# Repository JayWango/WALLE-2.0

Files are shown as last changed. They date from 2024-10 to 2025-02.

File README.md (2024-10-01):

<p float="left">
  
   
</p>

### Stereovideographic & Macromolecular Acquisition of Low-Light Emitters

The UCSB Oakley Evolution Lab seeks to investigate the evolutionary history of bioluminescence courtship signaling of small crustaceans called ostracods. Such emissions occur after nightfall when there is no moonlight and are characterized as pulses that vary in temporal and spatial patterns between species. We are creating a camera and DNA collection system named Stereovideographic & Macromolecular Acquisition of Low-Light Emitters (small-e), for deployment at the bottom of the Caribbean Sea. Small-e will capture stereo-vision video that will be stereo-rectified to create 4D models of the courtship patterns. We are aiming to have small-e be compact and to support new features compared to previous camera systems, such as time-precise light intensity measurements, time correspondent eDNA collection, and a 12-hour runtime. 

# External Behavioral Specification
The videography system will record stereo video footage of the ostracod courtship signaling. This data will be reconstructed into 3D models of the signals. Light intensity measurements of the signals will be made with a SiPM. This data will be output into a processable text file. The footage and light intensity measurements cause the DNA collector system to pump water through DNA collecting filters. The pump system will measure the amount of water processed to ensure proper collection.

## Low-Light Electrostereo Videography System
Stereo synchronized cameras will provide stereo vision video for reconstructing 3D bioluminescence courtship signaling of ostracods over time. This footage will be used to recognize patterns from courtship.

## DNA Collector System
At set timer intervals, a pump will push water through a filter to collect the DNA present in the water. 3 filters will be used to sample a total of 6L over the course of 12 hourss. The lab will be able to extract the ostracod DNA from the various species present in the water at different times corresponding to the video footage.

## Light Intensity Measurement
Detects the blue light intensity from the ostracod courtship signaling and outputs it into a file. Will help characterize the temporal patterns of the pulses among ostracod species. 

# Block Diagram 

small-e Block Diagram

# Team Member Responsibility 
- Ebony (Leader) - Programming the SiPM sensor to detect BioLuminescent light under water. Designing waterproof case suitable for SiPM Sensor.
- Reiley - Implementation of low-light, stereo camera system and synchronization.
- Roberto -  Designing DNA collector. Configuring the software interface of the pump system. Designing modular waterproof case for this system. 
- Ryan - Implementing user interface for utilizing the entire system as well as other general responsibilities, including the data storage system.
- Sammy - Implementation of low-light, stereo camera system and synchronization and SiPM.

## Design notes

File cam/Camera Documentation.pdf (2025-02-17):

## Watec 933 Camera Documentation

Curated by Dakota Barnes, 5/31/2024, dakota@casabarnes.com

1) New Camera Spreadsheet
https://docs.google.com/spreadsheets/d/1HkeTYAVQ3RaVRUFHyAiKlf5FlizRkfooBxWkuCNOLkc/edit#gid=0 (https://docs.google.com/spreadsheets/d/1HkeTYAVQ3RaVRUFHyAiKlf5FlizRkfooBxWkuCNOLkc/edit#gid=0)
2) Watec User Manual
https://drive.google.com/file/d/1hmxL5e7SJMkztWb8NpXOMxQa4R7WxiXF/view?usp=sharing (https://drive.google.com/file/d/1hmxL5e7SJMkztWb8NpXOMxQa4R7WxiXF/view?usp=sharing)
3) All_reset.bin
https://drive.google.com/file/d/1d34jDYIjwuBzf9ph53bu5fn5DB1mxrl5/view?usp=drive_link (https://drive.google.com/file/d/1d34jDYIjwuBzf9ph53bu5fn5DB1mxrl5/view?usp=drive_link)
4) Camera settings
https://drive.google.com/drive/folders/1ein_ycJGoXDxwvxqVLbZZHRgHMuEGonK?usp=drive_link (https://drive.google.com/drive/folders/1ein_ycJGoXDxwvxqVLbZZHRgHMuEGonK?usp=drive_link)

Quick Note

These settings were created in 2024 to get the SMALLE devices up and running. We spent a few weeks troubleshooting the cameras, as they were not able to connect. We got smalle 1.1 to work by just switching the left and right cameras, but we were not as lucky with Smalle 2 and 4. I believe the cause of the problems was that the cameras reset to default/previous IP addresses, which caused some conflicts when trying to connect them to the Jetson Nano. My advice for future engineers; just do the hard reset if you are spending too much time debugging. I was initially scared to do it but it is not as bad as it seems.

All Cameras Login for Accessing Settings (Typing IP address into connected browser)

Username = smalle

Password = smalle

Also current settings are just default, with brightness set to 15/20.

### A. Jetson/Camera Configurations

One of the changes that I made was to standardize the IP addresses across all left cameras, right cameras, and the Jetson IPv4 settings. Here is the table with the current camera information, and what their corresponding IP addresses should be.

Camera Physical Label | Side | Old Camera Label | SMALLE | Mac Address | Serial Number | Camera IP | Working
SMALLE 1 | LEFT | DNE | 1 | c4:7c:8d:30:62:70 | W51400625 | 192.168.0.250 | Yes
SMALLE 1 | RIGHT | DNE | 1 | c4:7c:8d:30:62:58 | W51400601 | 192.168.0.251 | Yes
SMALLE 4 Watec 8 | LEFT | oakley-watec5 | 4 | c4:7c:8d:30:63:38 | W51400825 | 192.168.0.250 | Yes
SMALLE 4 Watec 9 | RIGHT | oakley-watec4 | 4 | c4:7c:8d:30:63:37 | W51400824 | 192.168.0.251 | Yes
SMALLE 2 Watec 4 | LEFT | oakley-watec6 | 2 | c4:7c:8d:30:63:20 | W51400801 | 192.168.0.250 | Yes
SMALLE 2 Watec 5 | RIGHT | oakley-watec9 | 2 | c4:7c:8d:30:63:1F | W51400800 | 192.168.0.251 | Yes

Table 1: Camera Configurations

Notice all left cameras have assigned IP 192.168.0.250, and all right cameras have IP 192.168.0.251. This means that any right camera can be interchangeable, and any left cameras can be interchangeable.

In order for the Jetson to communicate with the cameras, it should also have the correct IPv4
settings configured for the left and the right cameras.
Smalle Label | Jetson Label | IPv4 Address | IPv4 Gateway | Software IP 1 | Software IP 2 | Camera Left | Camera Right | SSD Card
SMALLE 1.1 | SMALLE 2 | 192.168.0.100 | 192.168.0.1 | 192.168.0.250 | 192.168.0.251 | SMALLE1 LEFT | SMALLE1 RIGHT | SMALLE 1
SMALLE 4 | SMALLE 4 | 192.168.0.100 | 192.168.0.1 | 192.168.0.250 | 192.168.0.251 | SMALLE4 W.9 L | SM.4 W.8 R | SMALLE 4
SMALLE 2 | SMALLE 3 | 192.168.0.100 | 192.168.0.1 | 192.168.0.250 | 192.168.0.251 | SMALLE2 W.4 L | SMALLE2 W5 R | SMALLE 3

Table 2: Jetson Configurations

Notice the IPv4 address should be 192.168.0.100, and the IPv4 gateway should be 192.168.0.1

### B. TroubleShooting The Cameras

When we were working with the cameras, the most difficult problem to tackle was initially connecting them, as it might feel like a shot in the dark. Luckily, with the IP addresses above and the next section you should be able to get them connected. Here is the order I recommend troubleshooting.

### 1. Power

Make sure that the Buck converters are supplying 12V to the cameras through the power. Even though the ethernet port says PoE (power over ethernet), it has a different power source because the network switch and Nano don’t have the capabilities to power the cameras through Ethernet. You can confirm that the cameras are getting power by plugging them in for a few minutes, and they should be hot to the touch. Also, what worked for us once was switching the cameras around, but that could have been a fluke.

2. Jetson IPv4 address and IPv4 gateway.
Next, make sure that the Jetson Nano is configured to accept the correct IP address. Preferences → Network Connections → Wired Connection 1 → IPv4 Settings Method = manual, the IPv4 Address = 192.168.0.100, and the IPv4 Gateway = 192.168.0.1.

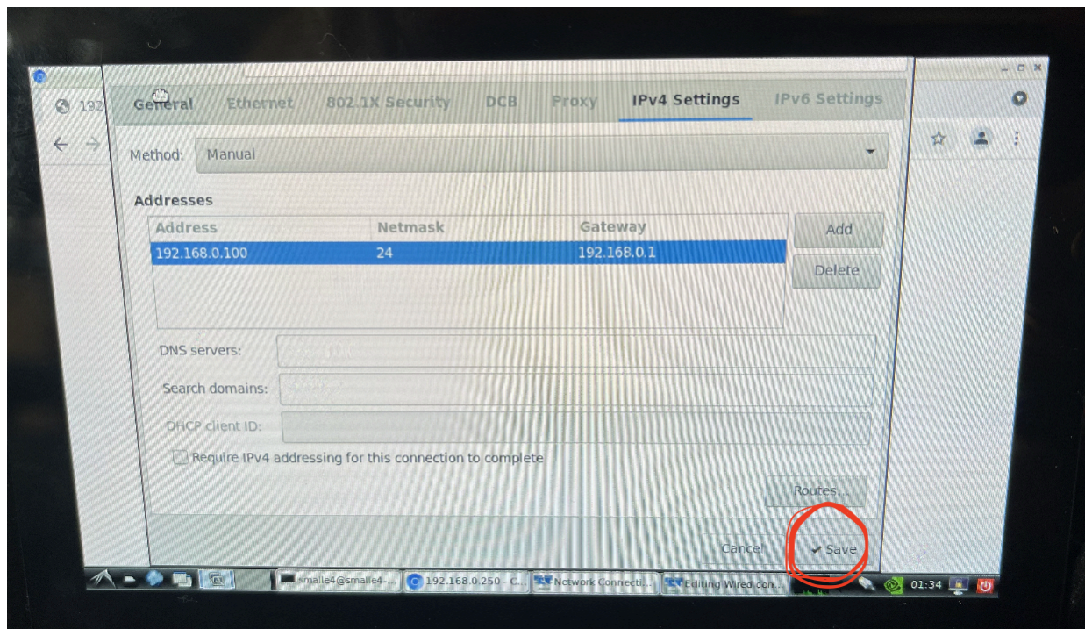
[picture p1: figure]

Picture 1: Jetson Nano IPv4 settings for Wired Connection

** Note, in the window you have to push the save button on the bottom right. It might not be visible so you have to “move” the screen using the options on the top left of the page

Once you do this, reboot the Jetson nano for the changes to take effect. To see if the cameras are connected, you can ping them individually with “ping 192.168.0.25X” in the terminal, where “X” is replaced with “0” (for the left camera) and “1” (for the right camera), and you should see packets coming through. If you are not getting anything through, I learned the hard way the next easiest thing to do is a hard reset.

### 3. Hard Reset

The easiest option to do next is to do a hard reset, which is explained in the Watec User Manual section 6.7 (link 1). It includes creating and copying a file (link 3) and placing it in the camera. For this I only had power plugged in, and not ethernet.

Once this hard reset is done, the IP address of the camera will revert to 192.168.1.250. Intentionally, this IP address will require the Jetson Nano to have a slightly different IPv4 address and IPv4 gateway, which you can change temporarily to connect to the camera with default settings.

To do this, go to the IPv4 Settings on the Jetson (location in B.2), and change the settings as follows.
Address = 192.168.1.100, Mask = 24, Gateway = 192.168.1.1

Once you add the temporary settings press save, and reboot the Jetson. You should be able to ping the camera in the terminal with “ping 192.168.1.250”. If not, your hard reset failed, your camera is broken, or you are going to have to go deeper in the rabbit hole than I did.

Go to chromium and type in the IP address into the browser 192.168.1.250. You should be directed to enter a username in password. Follow the instructions in the User Manual (link 2) section 6.1 to login to the Camera Settings, which is based on Serial Number and Mac Address.

***We Have Changed Username = smalle, Password = smalle *** You Have Two Options for how to Proceed to Change The IP Address:
i. Loading Default Settings
This is explained in step C, which will configure all the camera settings based on if it is a right or left camera. The benefit is that the IP address will be changed, and also the camera settings will be transferred like Brightness, camera mode, and other settings for filming the dark.
ii. Manually changing IP address
In the settings, view User Manual section 6.5 to change the IP address to what it is supposed to be in Table 1, based on left or right.

Final step. Once you change the IP address in the settings browser, you will no longer be able to connect to the camera with your Jetson IPv4 settings. This means that you will have to go back to step B2 in this document, to configure the Jetson settings to what they are supposed to be.

### C.Loading the Settings

This will ensure that we have settings that are the same across all cameras. I have included the settings for the camera in the google drive at link 4, just so they will be tracked for now on. Note that there are settings for the left and the right camera, which are copied from Smalle 1.1 cameras. To load/save the settings, follow the instructions in the User Guide section 6.2.4.

First thing to note is that the IP address might change on your camera, so your Jetson Nano IPv4 settings might have to be changed to the required ones in B2.

Second thing to note is that this will also change the password on your current camera (sorry). Below is a table with the relevant information.

Load Settings | Folder Name | Loaded IP Address | Loaded Password
Right Cameras | Right_251 | 192.168.0.251 | W5140060158
Left Cameras | Left_250 | 192.168.0.250 | W5140062570
Table 3: Loaded Camera Settings Information

I recommend changing the password back to the default to avoid confusion, which is in section 6.2.1 of the user manual. (New password is from the original 1.1 cameras).

When going through the load settings steps, it asks for your password but I found you can sometimes just cancel it, the process is a bit buggy. I recommend rebooting the nano after the settings are loaded.

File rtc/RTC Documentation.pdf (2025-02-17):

## Setting Up RTC

1. With DS3231 module, plug in the 3V lithium battery, with the engraving facing outward
2. Use female to female wires (unless you want to solder) in the following configuration
DS3231 SCL | → | Jetson Nano Port 3 SCL
DS3231 SDA | → | Jetson Nano Port 5 SDA
DS3231 GND | → | Jetson Nano Port 9? GND

*Note that because of the battery, we don’t plug in VCC (you can if you want)

3. Connect Jetson Nano to internet to download packages and get current time(ethernet)
a. Use USB to ethernet and configured port 4.1 062 D1 (Configured By Ted)
b. OR Bring to your own home internet and plug into ethernet
4. Download package smbus2 With the following command
a. sudo pip3 install smbus2 (might require installing pip)
i. sudo apt install python3-pip (if needed for pip)
5. Test to see if the DS3231 is connected by running command in terminal
a. sudo i2cdetect -y 1
b. If done properly you should see 0x68 in output
6. Try running the python scripts created using python3
a. rtc_read.py → will output the time on the rtc
b. rtc_write.py → will place the time from the nano, onto the rtc device

7. Set sudo settings to allow changing device time without password
a. sudo usermod -aG i2c username
i. So that password not needed for i2c communication
b. sudo visudo
i. Once editor is open, insert line:
1. ALL ALL=(ALL) NOPASSWD: /bin/date *, /sbin/hwclock * ii. This makes it so that no password needed for editing system time iii.
Notes:
- Remember to set your RTC time when connected to ethernet to get it setup
- Batteries supposedly last around 2 years, and are very cheap and easy to switch out

## Scripts for rtc

The python scripts will be in the SSD->WALLE-2.0->rtc Folder.
1. python3 rtc_read.py → will output(read) the time on the rtc module
2. python3 rtc_write.py → will place the time from the nano, onto the rtc device
3. python3 nano_setTimeRTX.py → will place time from the rtc device onto the nano's system clock. This is the script that runs at the beginning of control_loop.py (on startup).

## Manually Setting System Clock

The best way to set the nano’s system clock is to simply plug it into ethernet. However, if that is not an option, you can choose to manually set it with this command

1. Open the terminal on your Jetson Nano.

Use the date command to set the time. The format for the date command is:

### sudo date MMDDhhmm[[CC]YY][.ss]

2.
- MM is the month.
- DD is the day.
- hh is the hour in 24-hour format.
- mm is the minutes.
- CC is the first two digits of the year (optional).
- YY is the last two digits of the year (optional).
- .ss is the seconds (optional).

For setting the time to 9 PM, you will need to specify the date and time. For example, if today's date is July 10, 2024, you can set the system clock to 9 PM as follows:

### sudo date 07102100

This command sets the date to July 10 and the time to 21:00 (9 PM in 24-hour format).

3. (Optional) Apply your changes to the hardware clock, so the last seen time will be remembered when powered off and on. (Not needed with external rtc that we have).

$ sudo hwclock -w

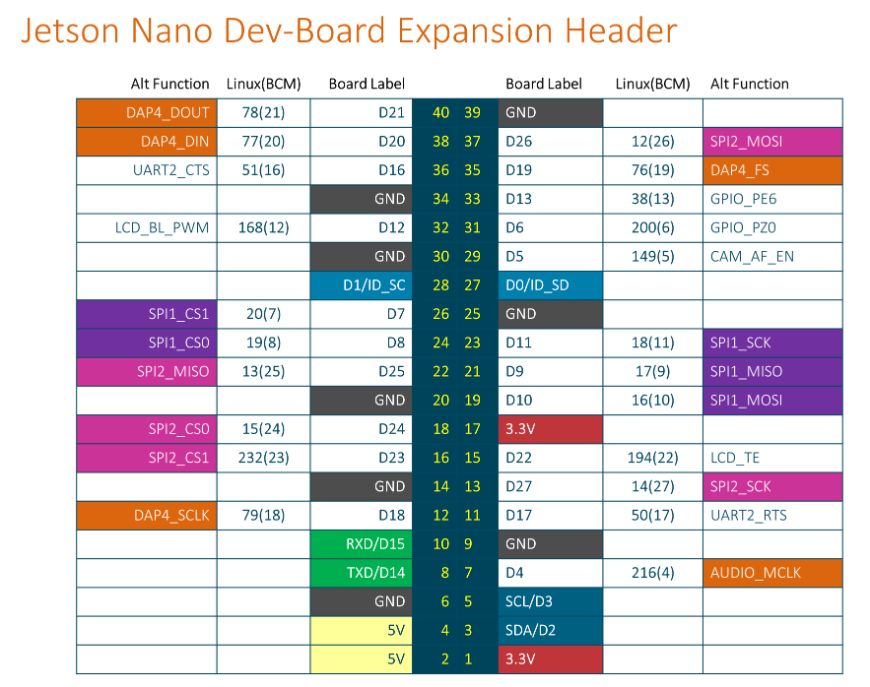
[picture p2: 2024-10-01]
pinouts.png

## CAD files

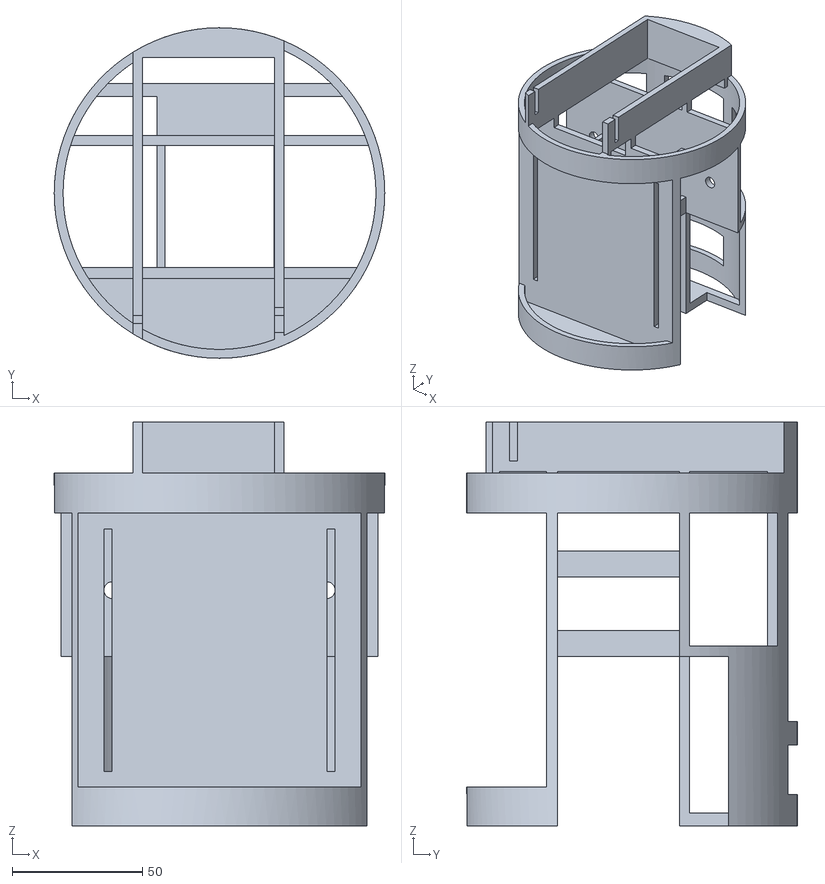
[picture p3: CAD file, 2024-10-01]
3D printing files/STL Files/Top Main Tray.stl
126.8 x 126.8 x 155.0

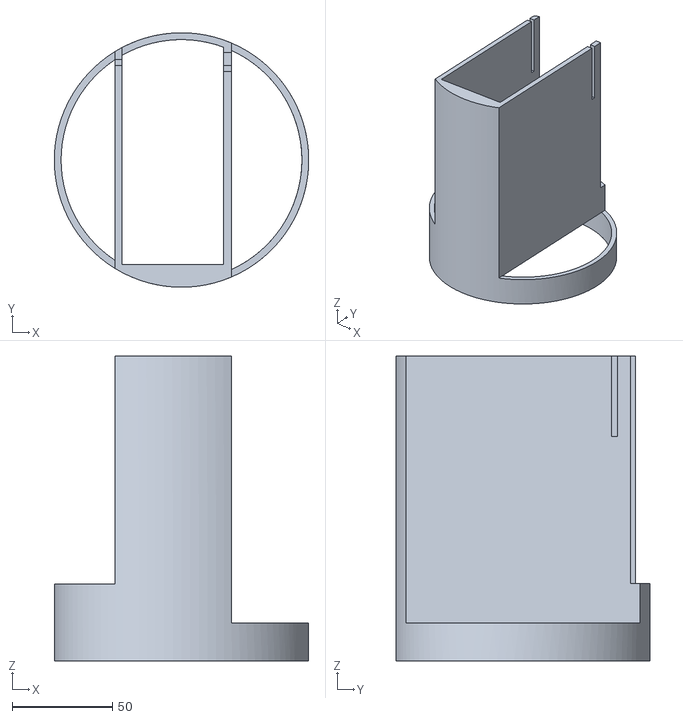
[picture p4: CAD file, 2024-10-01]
3D printing files/STL Files/Bottom Main Tray.stl
126.8 x 126.8 x 152.0

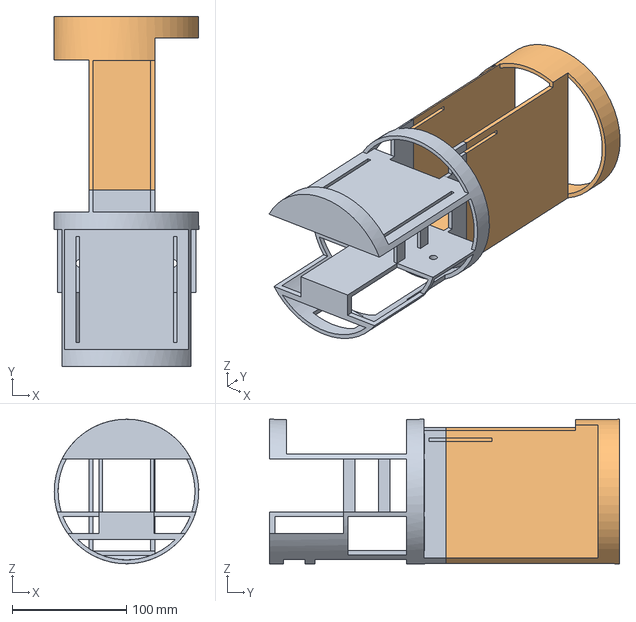
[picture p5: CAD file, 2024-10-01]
3D printing files/CAD Files/smalle Main Tray Original Lens.step
126.8 x 307.0 x 126.8 mm

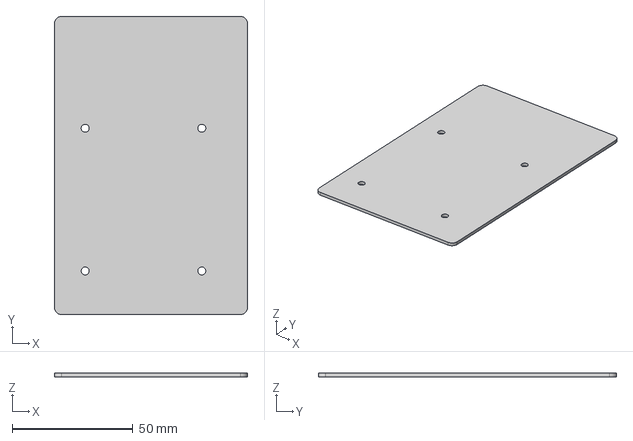
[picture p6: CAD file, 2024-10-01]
3D printing files/CAD Files/screen.step
79.9 x 123.5 x 1.50 mm

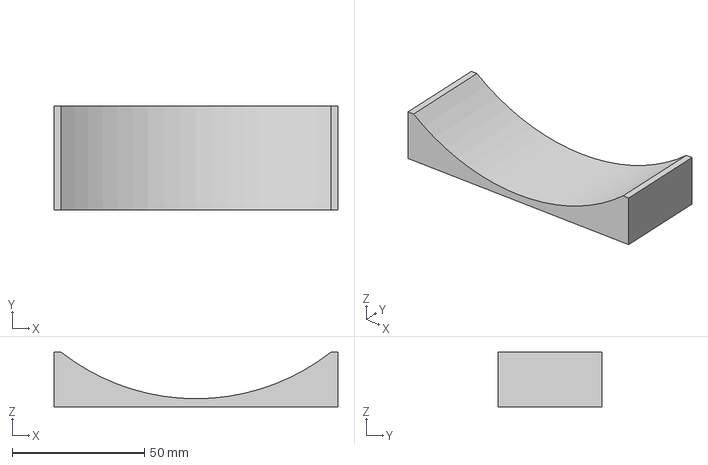
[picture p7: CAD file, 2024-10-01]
3D printing files/CAD Files/Case Stand Sideways.step
107.2 x 39.4 x 20.6 mm

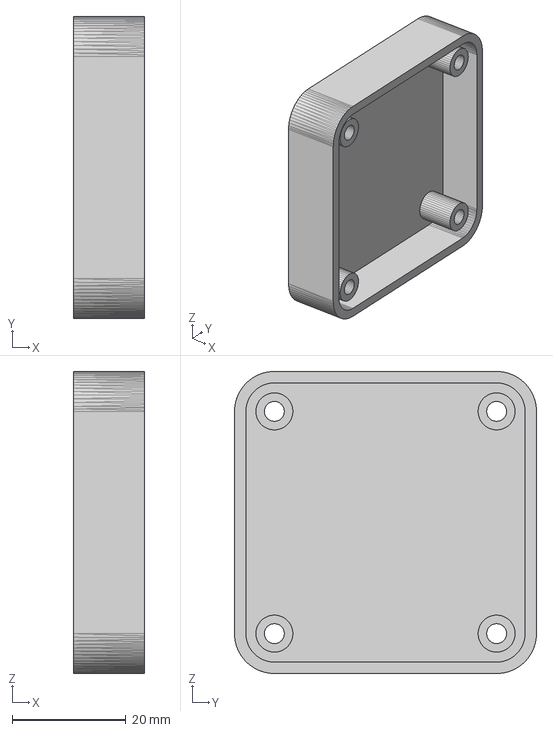
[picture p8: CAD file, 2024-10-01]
3D printing files/CAD Files/Botblox Case Short.step
12.4 x 53.0 x 53.0 mm

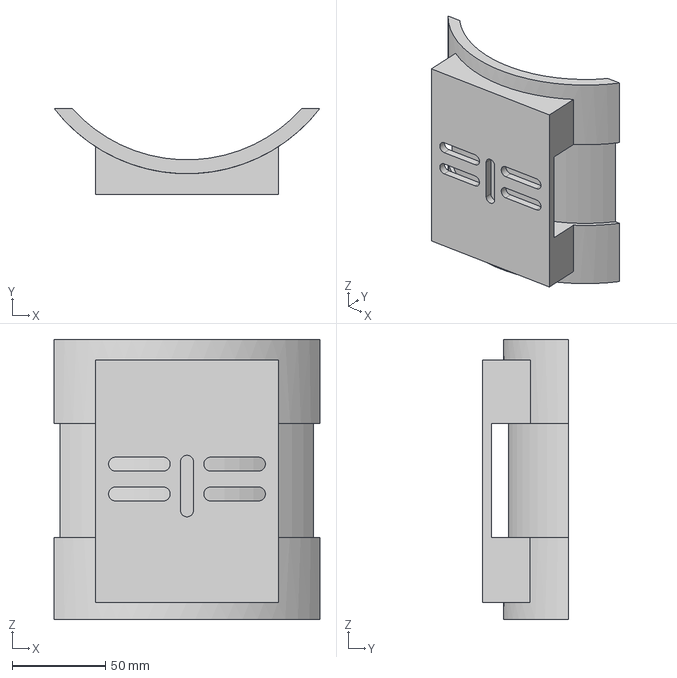
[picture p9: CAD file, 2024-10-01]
3D printing files/CAD Files/Tripod Mount Tray.step
142.5 x 46.2 x 150.0 mm

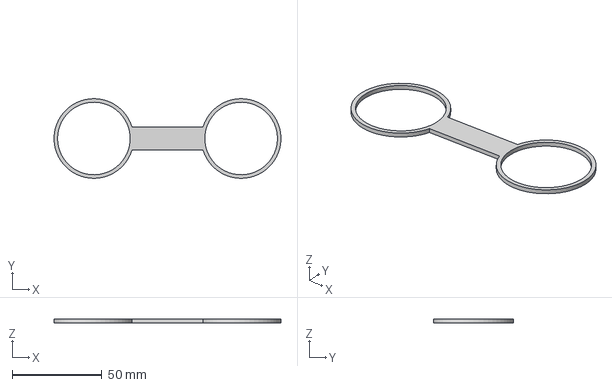
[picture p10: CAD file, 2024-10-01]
3D printing files/CAD Files/Lens Covers.step
126.7 x 44.5 x 2.00 mm

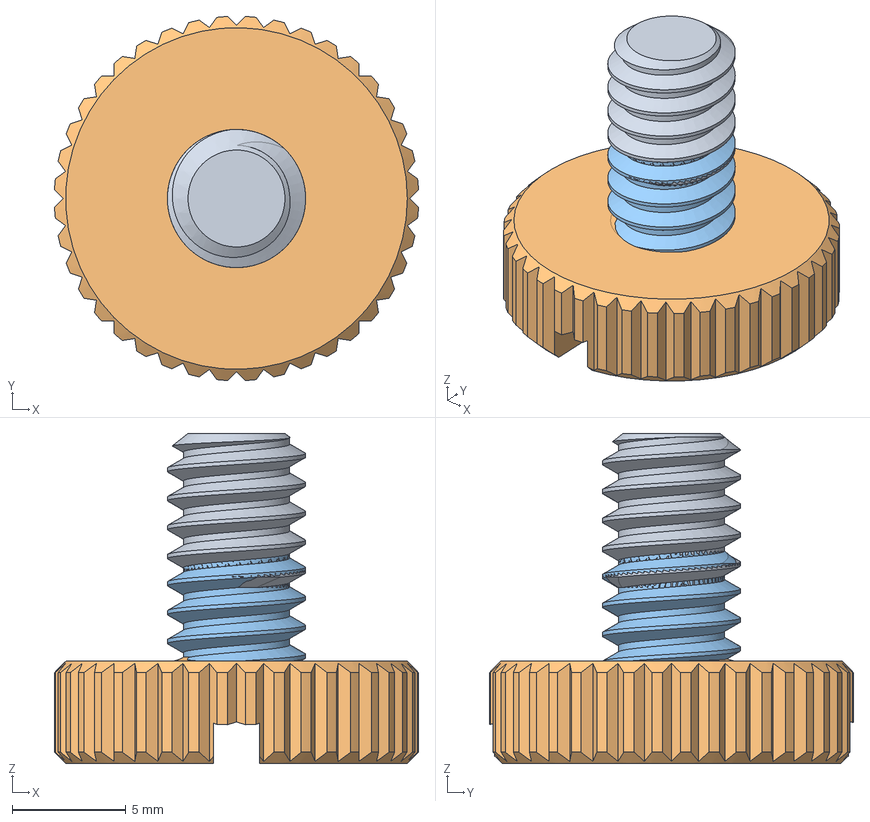
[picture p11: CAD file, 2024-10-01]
3D printing files/CAD Files/Camera Screw.step
16.0 x 16.0 x 14.5 mm

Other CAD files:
3D printing files/STL Files/Botblox Case Short.stl
3D printing files/STL Files/Camera Screw.stl
3D printing files/STL Files/Case Stand Sideways.stl
3D printing files/STL Files/Lens Covers.stl
3D printing files/STL Files/Tripod Mount Tray.stl
3D printing files/STL Files/screen.stl

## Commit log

2024-07-07 Add Smalle3 SSD to git, (has some new RTC changes
    [Botblox Case Short.step, Botblox Case Short.stl, Bottom Main Tray.stl, Camera Screw.step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]
2024-07-11 Add RTC documentation, and update camera documentation
2024-10-01 Adding SMALLE2 branch from SSD to github
    [Botblox Case Short.step, Botblox Case Short.stl, Bottom Main Tray.stl, Camera Screw.step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]
2025-02-19 modifying preview shell file for single camera setup
2025-02-20 changing aspect ratio of preview camera feed
2025-02-20 check for ip address of connected camera and run either left or right gstreamer pipeline
2025-02-21 testing ways to check if camera is connected
2025-02-21 implementing camera connectivity function
